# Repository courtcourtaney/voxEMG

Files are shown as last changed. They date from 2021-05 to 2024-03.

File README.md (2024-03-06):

------------

# VoxEMG (v3.1)

## About
<p>This repository contains information and all the editable project files for the VoxEMG project. VoxEMG is a pre-amplificaton circuit developed specifically for surface electromyography (sEMG) of the small extrinsic laryngeal muscles, but can be used on other muscles. <br>
	
The VoxEMG circuit is an extension of the open-source [EMG Circuit v7.1 (Advancer Technologies)](advancertechnologies.com/p/muscle-sensor-emg-circuitkit-bronze.html), from which other EMG platforms such as the Myoware are derived. VoxEMG is specifically aimed to detect activation of the extrinsic laryngeal muscles in both vocalised and subvocalised singing. High-precision and trimmable resistors are used to ensure noise reduction and the circuit is flexible to be used with different types of electrodes for desired implementation. The EMG signals can then be used in a variety of manners, for instance to relay feedback about the singer's movements during practice. <br>

This is an ongoing body of work with origins in my PhD thesis, [Imagining & Sensing: Understanding and Extending the Vocalist-Voice Relationship Through Biosignal Feedback](https://www.courtneynreed.com/assets/pdf/Reed_PhD_ImaginingSensing.pdf), which contains details on how the circuit and sonified EMG biofeedback has been used in vocal practice. I am always adding more information and designs, so please keep an eye out for updates, new implementations and improvements, and feel free to get in contact at any time regarding the project, what you're working on with it, and anything I can help with at: [c.n.reed@lboro.ac.uk](mailto:c.n.reed@lboro.ac.uk) </p>

## Versions

The schematics and PCB designs have been created in and are editable in [KiCad](http://kicad-pcb.org). Please feel free to adapt them to your needs and share your designs with me if you like!

### v3.1 - eTextile Configuration
[Version Subfolder Here](https://github.com/courtcourtaney/voxEMG/tree/master/VoxEMG-v3.1)

The current version's (v3.1) configuration of the circuit is designed for implementations in wearables, featuring mounting loops in the PCB for securing the board to textile structures and castellated inputs (designed by Adan Benito and Becky Stewart for the [Bela E-textile Capelet](https://oshpark.com/shared_projects/y0oSowUt) on Innovate UK), for conductive thread inputs. <br>

<p align="center">
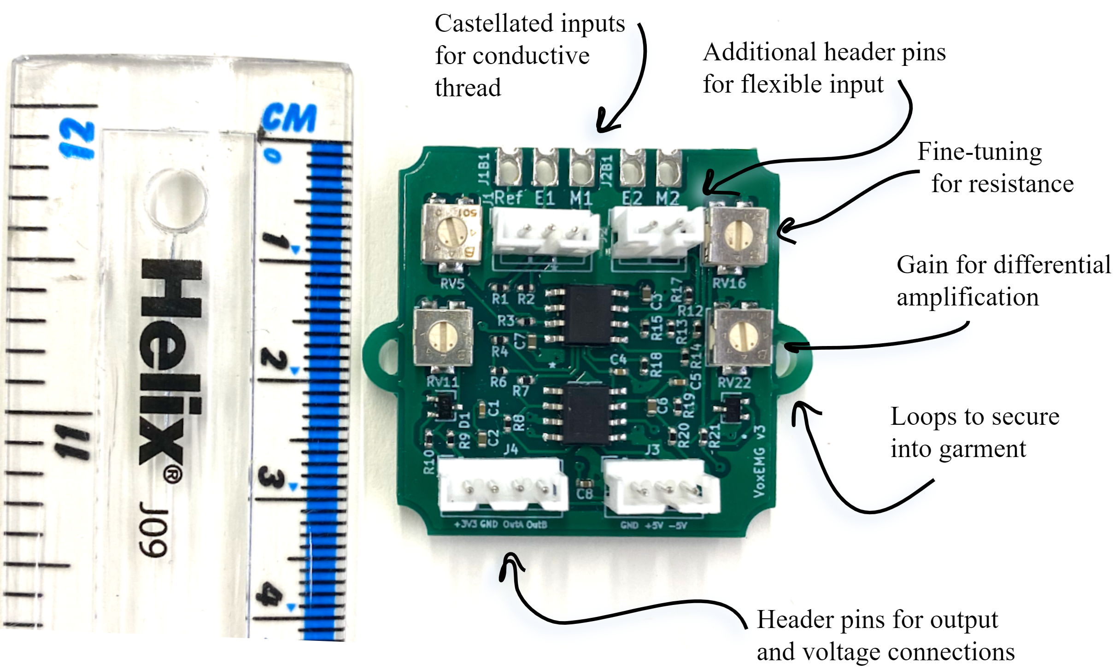
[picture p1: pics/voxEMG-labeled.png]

</p>

### v3.1.2 - Bela Mini Capelet
[Version Subfolder Here](https://github.com/courtcourtaney/voxEMG/tree/master/VoxEMG-v3.1.2)

<p>The latest PCB design (v3.1.2) features the same circuit implemented to be compatible with the Bela Mini embedded audio platforms. This setup is designed to be plug and play, with EMG being received directly on the A0 and A1 analogue inputs of the Bela Mini, and uses similar Molex connectors for electrode inputs. </p>

The design of this v3.1.2 capelet was supported by [Sound & Music UK's New Voices 2022](https://soundandmusic.org/compose/new-voices-2022/) with vocalist Lou Barnell as part of the piece [<em>To Fly Out in the Heat of Day</em>](https://loubarnell.co.uk/TO-FLY-OUT-IN-THE-HEAT-OF-DAY) - thank you!

<p align="center">
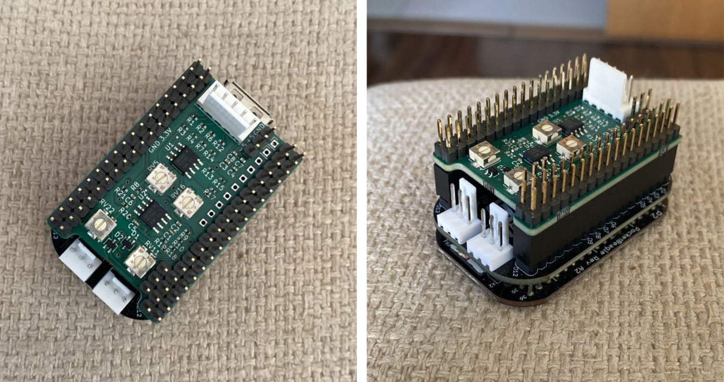
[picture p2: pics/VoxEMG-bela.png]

</p>

## Building the Circuit
If you are interested in getting a VoxEMG board, get in contact - I'm happy to help with any sEMG and vocal projects related projects and I can supply PCBs depending on the project. If you wish to make your own board, it is relatively in-expensive and easy to build the circuit yourself and try it out. A Bill of Materials (BOM) can be found in each version's folder in the file *EMGSensor3.1_bom.xlsx* or listed out below. The setup described here is for single-circuit dual muscle measurement; if you wish to only measure one muscle, you need only use one side of the ICs: <br>

Parts[^1]

* 2x [Texas Instruments OPA1612 op amp](https://www.ti.com/product/OPA1612) <br>
* 5x [Surface cup electrodes](https://www.pulsemedical.co.uk/store/Gold-Reusable-10mm-EEG-Cup-Electrodes-Pack-of-10-Wire-150cm-p79620827)[^2] <br>
* 2x 9V batteries + straps <br>
* Breadboard <br>
* Jumper wires <br>
* Microcontroller of choice or, in our case, a [**Bela**](bela.io)! <br>
* Resistors: <br>
	* 4x 10k Ω 0.1% precison <br>
	* 4x 100k Ω 0.1% precison <br>
	* 2x 100 Ω <br>
	* 2x 1k Ω <br>
	* 6x 10k Ω <br>
	* 2x 100k Ω <br>
	* 2x 150k Ω <br>
* Trimpots/Variable Resistors:<br>
	* 2x 500 Ω <br>
	* 2x 100K Ω <br>
* Capacitors:<br>
	* 1x 0.1 uF ceramic <br>
	* 4x 10 uF ceramic <br>
	* 2x 2.2 nF ceramic <br>
* 2x Schottky 40V 120mA diodes <br><br>

The KiCad project containing the VoxEMG schematics and board layout can be found in the folder for each version *VoxEMG-v3.1,* for the textile-integrated board or *VoxEMG-v3.1.2,* for the Bela Mini capelet, otherwise using the following schematic (v3.1). This schematic depicts use of one side of the ICs - for the second muscle, the connections should be duplicated on the other side. See *VoxEMG-v3.1/EMGSensor3.1.sch* for the full schematic. </p><br>

<p align="center">
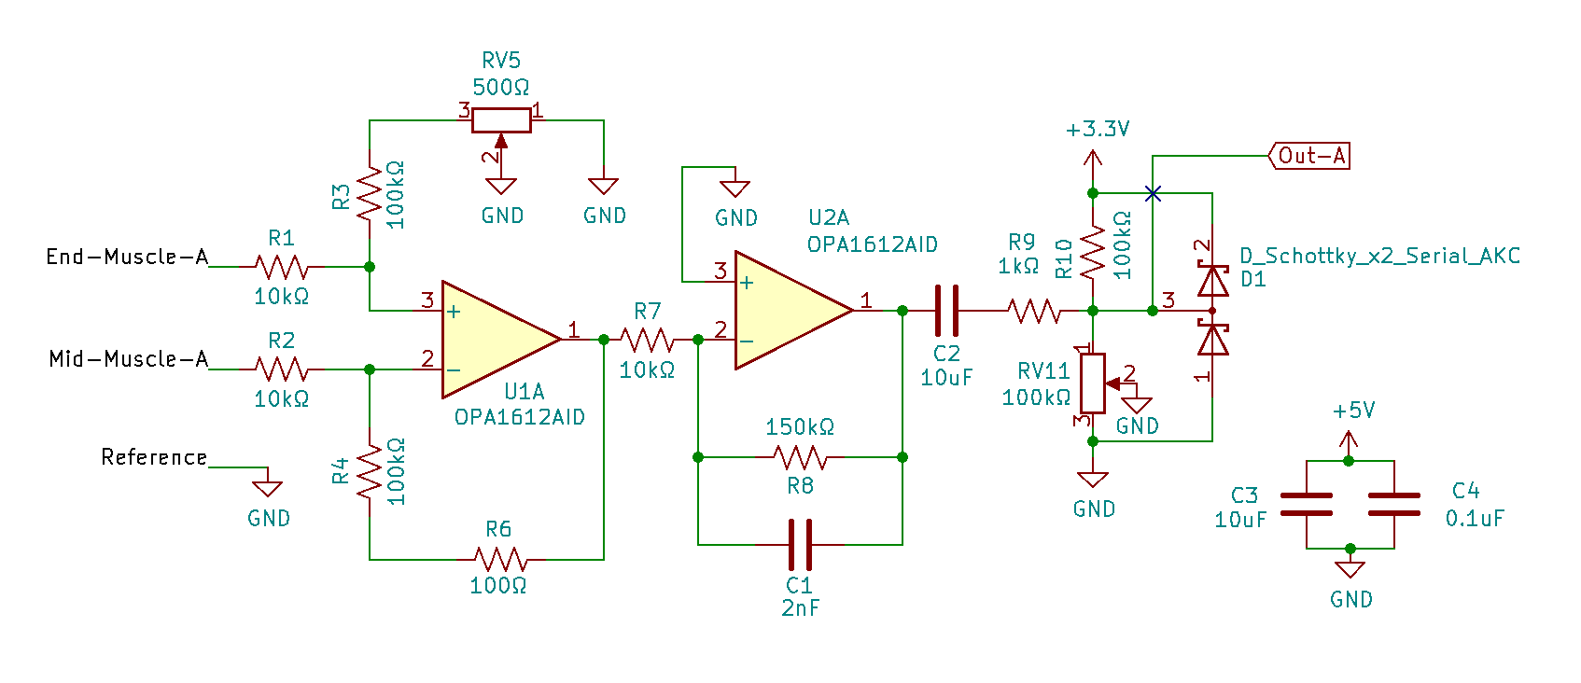
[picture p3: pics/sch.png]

</p>

<!-- *Some notes:* <br> -->
[^1]: Additionally (and especially if you use reusable electrodes), you will need to purchase some adhesive conductive paste (we recommend [Ten20](https://www.pulsemedical.co.uk/store/Ten20-Conductive-Paste-228g-jars-3-pack-10-20-8-p69723951)) and flexible non-woven fabric tape to help secure the electrodes (we use [Hypafix](https://www.bsnmedical.com/products/wound-care-vascular/category-product-search/acute-wound-care/fixation/hypafixr-transparent.html)).

[^2]: These reusable gold-plated silver electrodes use a DIN adaptor intended for use with medical EMG devices; cut these off and you can use either alligator clips to connect these, or solder a male pin to the end of the cable so you can use it in a breadboard or within another cable assembly, such as the Molex connectors implemented in v3.1.2.

<!-- VoxEMG PCB layout          | VoxEMG board
:-------------------------:|:-------------------------:
![](https://github.com/courtcourtaney/voxEMG/blob/master/pics/PCB.png)  |  ![](https://github.com/courtcourtaney/voxEMG/blob/master/pics/3Drender.png) -->

## Example Use
<p>Electrodes will need to be affixed to the muscle site, for instance on the suprahyoid digastric muscle here.</p><br>

<p align="center">

</p>

<p>
We use a Bela for collection of voltages from the EMG, and so the code included here is also for Bela - it is fine to use another microcontroller, so long as you're ok with implementing some simple digital filtering. In this case, we use the analog inputs on Bela.</p><br>

Bela handles some additional filtering of the EMG signal, including:<br>
- DC offset removal (from the DC signal introduced in the voltage divider)<br>
- Notch filtering to remove power line interference (**50Hz** UK - keep in mind if you need to change this wherever you are in the world!)<br>

As well, our setup for studies includes:<br>
- Text file output containing voltages over time<br>
- Setup for a button to be added so the vocalist can press during singing, helping with data/audio synchronisation<br>
You can, of course, comment this out (and it's marked as such in the code).

[Example Code Here](https://github.com/courtcourtaney/voxEMG/tree/master/examples)

## Projects Using the VoxEMG

If you have used the circuit or designs for your project, please let us know so we can add you here!

### Vocal Performances & Collaborations

[<em>To Fly Out in the Heat of Day</em>](https://loubarnell.co.uk/TO-FLY-OUT-IN-THE-HEAT-OF-DAY). Lou Barnell. 2023-2024. Performed in the UK & EU ([Based in Sheffield](https://www.theatredeli.co.uk/Event/enddateto-fly-out-in-the-heat-of-the-day)).

### Research Work & Papers
<span style="font-size:2em;"> 

Courtney N. Reed and Andrew P. McPherson. 2023. <em>The Body as Sound: Unpacking Vocal Embodiment through Auditory Biofeedback.</em> In Proceedings of the Seventeenth International Conference on Tangible, Embedded, and Embodied Interaction (TEI '23). Association for Computing Machinery, New York, NY, USA, Article 7, 1–15. https://doi.org/10.1145/3569009.3572738 [[PDF]](https://www.courtneynreed.com/assets/pdf/Reed_TEI23_BodyAsSound.pdf) <br>

Courtney N. Reed, Sophie Skach, Paul Strohmeier, and Andrew P. McPherson. 2022. <em>Singing Knit: Soft Knit Biosensing for Augmenting Vocal Performances.</em> In Proceedings of the Augmented Humans International Conference 2022 (AHs '22). Association for Computing Machinery, New York, NY, USA, 170–183. https://doi.org/10.1145/3519391.3519412 [[PDF]](https://www.courtneynreed.com/assets/pdf/Reed_AHs22_SingingKnit.pdf) <br>

Courtney N. Reed and Andrew P. McPherson. 2021. <em>Surface Electromyography for Sensing Performance Intention and Musical Imagery in Vocalists.</em> In Proceedings of the Fifteenth International Conference on Tangible, Embedded, and Embodied Interaction (TEI '21). Association for Computing Machinery, New York, NY, USA, Article 22, 1–11. https://doi.org/10.1145/3430524.3440641 [[PDF]](https://www.courtneynreed.com/assets/pdf/Reed_TEI21_sEMGPerformance.pdf) <br>

Courtney N. Reed and Andrew P. McPherson. 2020. <em>Surface Electromyography for Direct Vocal Control.</em> In Proceedings of the International Conference on New Interfaces for Musical Expression (NIME), July 21-25, Birmingham, UK, pp. 458–463. Birmingham Conservatoire, Birmingham, UK. https://doi.org/10.5281/zenodo.4813475 [[PDF]](https://www.courtneynreed.com/assets/pdf/Reed_NIME20_VocalsEMG.pdf) <br>
	
</span>

<br>

## Licensing
<p><br /><span xmlns:dct="http://purl.org/dc/terms/" property="dct:title">VoxEMG</span> by <span xmlns:cc="http://creativecommons.org/ns#" property="cc:attributionName">Courtney N. Reed & Andrew P. McPherson</span> is licensed under a <a rel="license" href="http://creativecommons.org/licenses/by-sa/4.0/">Creative Commons Attribution-ShareAlike 4.0 International License</a>. <br>

In the spirit of open-access research, VoxEMG and the circuit/PBC designs included here are are licensed under a Creative Commons Attribtion Sharealike license, or [CC-BY-SA](https://creativecommons.org/licenses/by-sa/3.0/). The information here is free to use and edit, so long as you provide credit and release your resulting work under the same license. This means you are free to edit and use these designs, as long as you agree to supply credit and release your results under the same license. <br>

If you use these designs or reference them, we ask that you please also cite the following papers in your work: <br>

If you want to create a commercial product using the VoxEMG hardware designs and don't want to release it under the same license, you will need a commercial license. Please email me at [c.n.reed@lboro.ac.uk](mailto:c.n.reed@lboro.ac.uk) to enquire further. </p>

```latex
@inproceedings{Reed_AHs22_SingingKnit,
  title = {{Singing Knit: Soft Knit Biosensing for Augmenting Vocal Performances}},
  author = {Reed, Courtney N. and Skach, Sophie and Strohmeier, Paul and McPherson, Andrew P.},
  year = {2022},
  month = mar,
  booktitle = {{Proceedings of the Augmented Humans International Conference 2022}},
  location = {Kashiwa, Chiba, Japan},
  publisher = {Association for Computing Machinery},
  address = {New York, NY, USA},
  series = {AHs '22},
  pages = {170–183},
  doi = {10.1145/3519391.3519412},
  isbn = {9781450396325},
  url = {https://doi.org/10.1145/3519391.3519412},
  numpages = {14},
  keywords = {wearables, Design, singing, music performance, knit, electromyography, fabric sensors, biosignals},
}
```

```latex
@inproceedings{Reed_NIME20_VocalsEMG,
  title = {{Surface Electromyography for Direct Vocal Control}},
  author = {Reed, Courtney N. and McPherson, Andrew},
  year = {2020},
  month = jul,
  booktitle = {{Proceedings of the International Conference on New Interfaces for Musical Expression}},
  publisher = {Birmingham City University},
  address = {Birmingham, UK},
  pages = {458--463},
  doi = {10.5281/zenodo.4813475},
  issn = {2220-4806},
  url = {https://www.nime.org/proceedings/2020/nime2020_paper88.pdf},
  editor = {Michon, Romain and Schroeder, Franziska},
  presentation-video = {https://youtu.be/1nWLgQGNh0g},
}
```

<!-- 
## To-Do List
There's a lot left to done, but at least for this repository, I'm planning on adding more information, including:<br>
- [x] Include editable schematics and PCB design<br>
- [ ] Step-by-step construction of the circuit<br>
- [ ] Walk-through of identifying laryngeal muscles <br>(feel free to contact me and I will help you via Zoom/Skype if you'd like to learn to do this on yourself!)<br>
- [ ] Add example Supercollider interfacing for sonification of signals/fun<br> -->

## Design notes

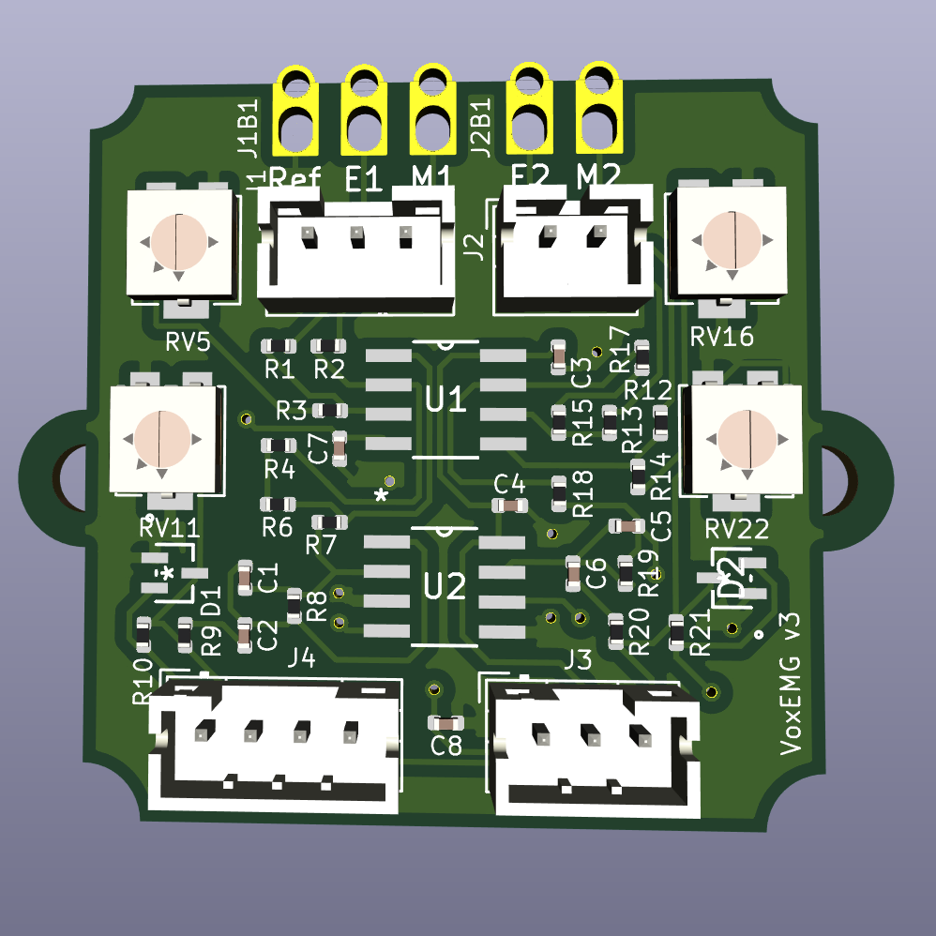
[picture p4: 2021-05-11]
pics/3Drender.png

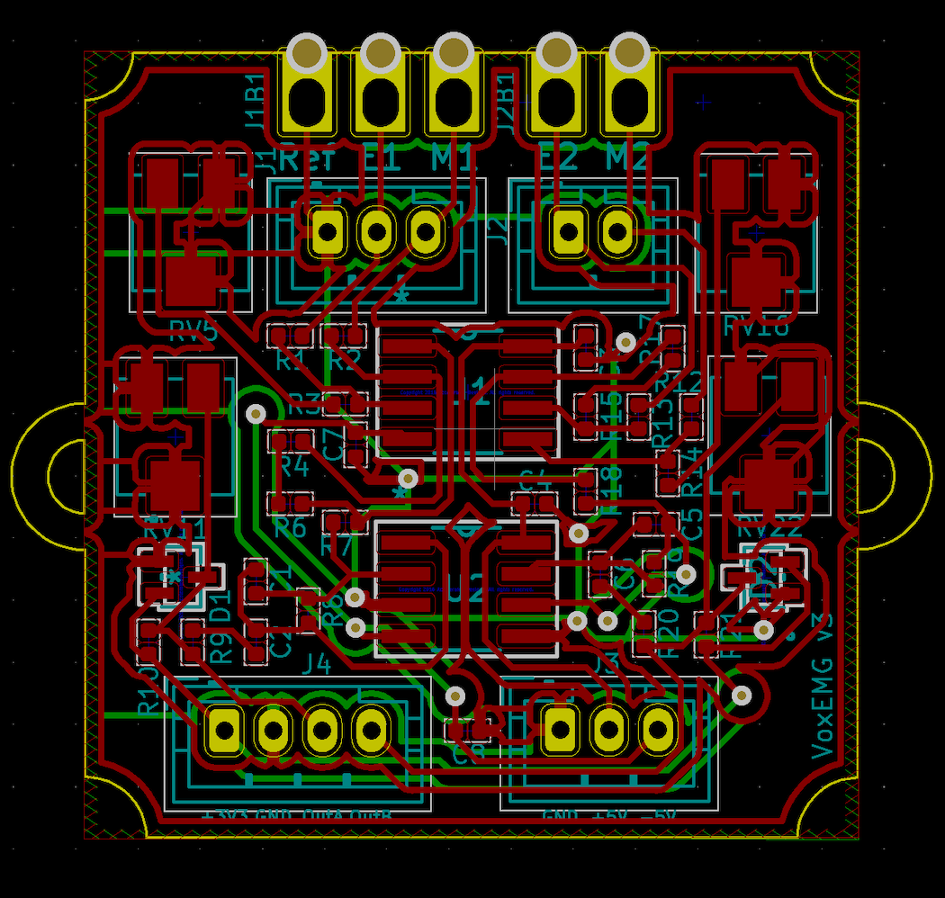
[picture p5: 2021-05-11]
pics/PCB.png

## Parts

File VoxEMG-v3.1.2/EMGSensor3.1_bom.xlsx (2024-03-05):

Name | Quantity | Value | Package | Description | Mouser # | Digi-Key # | Datasheet / Notes
U2, U1 | 2 | OPA1612AID | SOIC-8 | OPA1612AID | 595-OPA1612AID
D1, D2 | 2 | Schottky 40V 120mA | SOT-323-3 | BAS40-04 Schottky diode | 771-BAS40-04W-T/R
C1, C5 | 2 | 2.2nF | "0402" | Capacitor ceramic 0402 | 581-04023C222J4T2A
C8, C4 | 2 | 0.1uF | "0402" | Capacitor ceramic 0402 | 581-04023C104KAT2A62
C2, C3, C6, C7 | 4 | 10uF | "0402" | Capacitor ceramic 0402 | 581-0402ZD106MAT2A
R1, R2, R12, R13 | 4 | 10kOhm | "0402" | Resistor 0402 0.1% | 279-CPF-A-0402B10KE
R3, R4, R14, R15 | 4 | 100kOhm | "0402" | Resistor 0402 0.1% | 279-CPF-A0402B100KE1
R6, R17 | 2 | 100Ohm | "0402" | Resistor 0402 | 603-RP0402BRD07100RL
R7, R18 | 6 | 10kOhm | "0402" | Resistor 0402 | 603-RT0402FRE0710KL
R8, R19 | 2 | 150kOhm | "0402" | Resistor 0402 | RT0402FRE07150KL
R9, R20 | 2 | 1kOhm | "0402" | Resistor 0402 | RT0402FRE071KL
R10, R21 | 2 | 100kOhm | "0402" | Resistor 0402 | 603-RT0402FRE07100KL
RV5, RV16 | 2 | 500Ohm | SMD | Bourns 3314J vertical trim potentiometer | 652-3314J-1-501G
RV22, RV11 | 2 | 100kOhm | SMD | Bourns 3314J vertical trim potentiometer | 652-3314J-1-104E
J1 | 2 | Conn 01x05 | Through-hole | Molex K254 22-27-2051 5-pin male header | 538-22-27-2051
J3, J5, J6, J7, J8, J9, J10 | 7 | Connector_PinHeader | Through-hole | 2mm 01x01 vertical pin header | 910-HDR100IMP40MGVTH

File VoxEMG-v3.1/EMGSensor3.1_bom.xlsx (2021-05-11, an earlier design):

Name | Quantity | Value | Package | Description | Mouser # | Digi-Key # | Datasheet / Notes
U2, U1 | 2 | OPA1612AID | SOIC-8 | OPA1612AID | 595-OPA1612AID
D1, D2 | 2 | Schottky 40V 120mA | SOT-323-3 | BAS40-04 Schottky diode | 771-BAS40-04W-T/R
C1, C5 | 2 | 2.2nF | "0402" | Capacitor ceramic 0402
C8, C4 | 2 | 0.1uF | "0402" | Capacitor ceramic 0402
C2, C3, C6, C7 | 4 | 10uF | "0402" | Capacitor ceramic 0402
R1, R2, R12, R13 | 4 | 10kOhm | "0402" | Resistor 0402 0.1% | 279-CPF-A-0402B10KE
R3, R4, R14, R15 | 4 | 100kOhm | "0402" | Resistor 0402 0.1% | 279-CPF-A0402B100KE1
R6, R17 | 2 | 100Ohm | "0402" | Resistor 0402
R7, R18 | 6 | 10kOhm | "0402" | Resistor 0402
R8, R19 | 2 | 150kOhm | "0402" | Resistor 0402
R9, R20 | 2 | 1kOhm | "0402" | Resistor 0402
R10, R21 | 2 | 100kOhm | "0402" | Resistor 0402
RV5, RV16 | 2 | 500Ohm | SMD | Bourns 3314J vertical trim potentiometer | 652-3314J-1-501G
RV22, RV11 | 2 | 100kOhm | SMD | Bourns 3314J vertical trim potentiometer | 652-3314J-1-104E
J1, J3 | 2 | Conn 01x03 | Through-hole | Connector Header 3 position 2.00mm |  | A98589-ND
J2 | 1 | Conn 01x02 | Through-hole | Connector Header 2 position 2.00mm |  | A98588-ND
J4 | 1 | Conn 01x04 | Through-hole | Connector Header 4 position 2.00mm |  | A98590-ND

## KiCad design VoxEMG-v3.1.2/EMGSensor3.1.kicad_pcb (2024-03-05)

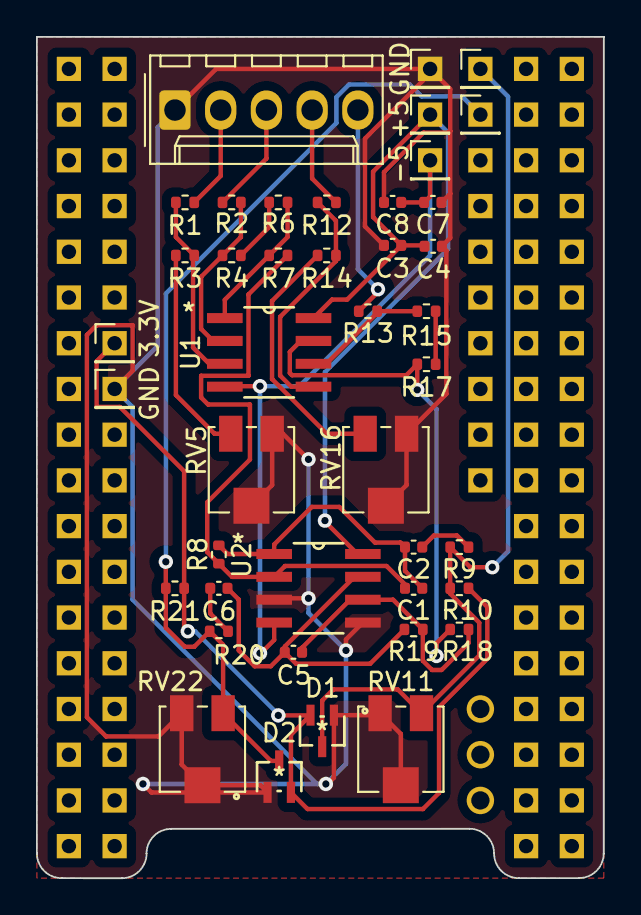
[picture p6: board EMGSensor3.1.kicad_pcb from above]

Board: 2 copper layers, 31.5 x 46.7 mm, 42 parts (0 on the bottom side), 26 nets.

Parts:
3.3V: +3.3V; PinHeader_1x01_P2.00mm_Vertical
+5: +5V; PinHeader_1x01_P2.00mm_Vertical
-5: -5V; PinHeader_1x01_P2.00mm_Vertical
C1: 2nF; C_0402_1005Metric
C2, C3, C6, C7: 10uF; C_0402_1005Metric
C4, C8: 0.1uF; C_0402_1005Metric
C5: 2.2nF; C_0402_1005Metric
D1, D2: D_Schottky_x2_Serial_AKC; BAS40-04W
GND: BelaGND; PinHeader_1x01_P2.00mm_Vertical
GND#2: BatteryGND; PinHeader_1x01_P2.00mm_Vertical
J1: Conn_01x03_Female; Molex_KK-254_AE-6410-05A_1x05_P2.54mm_Vertical
J5: Out-A; PinHeader_1x01_P2.00mm_Vertical
J6: Out-B; PinHeader_1x01_P2.00mm_Vertical
R1, R2, R7, R12, R13, R18: 10kΩ; R_0402_1005Metric
R3, R4, R10, R14, R15, R21: 100kΩ; R_0402_1005Metric
R6, R17: 100Ω; R_0402_1005Metric
R8, R19: 150kΩ; R_0402_1005Metric
R9, R20: 1kΩ; R_0402_1005Metric
RV5, RV16: 500Ω; Potentiometer_Bourns_3314J_Vertical
RV11, RV22: 100kΩ; Potentiometer_Bourns_3314J_Vertical
U1, U2: OPA1612AID

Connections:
+3.3V: 3.3V.1, D1.2 (K), D2.2 (K), R10.1, R21.1
+5V: +5.1, C3.1, C4.2, U1.8 (V+), U2.8 (V+)
-5V: -5.1, C7.2, C8.2, U1.4 (V-), U2.4 (V-)
/End-Muscle-A: J1.2, R1.2
/End-Muscle-B: J1.4, R12.2
/Mid-Muscle-A: J1.3, R2.2
/Mid-Muscle-B: J1.5, R13.2
GND: C3.2, C4.1, C7.1, C8.1, D1.1 (A), D2.1 (A), GND.1, GND#2.1, J1.1, RV5.1, RV5.2, RV11.2, RV11.3, RV16.1, RV16.2, RV22.2, RV22.3, U2.3 (+), U2.5 (+)
unnamed: C1.2, C2.2, R8.2, U2.1
unnamed: C2.1, R9.1
unnamed: C5.2, C6.2, R19.2, U2.7
unnamed: C6.1, R20.1
unnamed: R3.2, RV5.3
unnamed: R4.1, R6.2
unnamed: R6.1, R7.2, U1.1
unnamed: R14.2, RV16.3
unnamed: R15.1, R17.2
unnamed: R17.1, R18.2, U1.7
unnamed: R1.1, R3.1, U1.3 (+)
unnamed: R2.1, R4.2, U1.2 (-)
unnamed: R12.1, R14.1, U1.5 (+)
unnamed: R13.1, R15.2, U1.6 (-)
unnamed: C1.1, R7.1, R8.1, U2.2 (-)
unnamed: C5.1, R18.1, R19.1, U2.6 (-)
Out-A: D1.3 (common), J5.1, R9.2, R10.2, RV11.1
Out-B: D2.3 (common), J6.1, R20.2, R21.2, RV22.1

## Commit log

2020-07-24 Add files via upload
    add circuit schematics
    [EMGSensor2.2.sch]
2020-08-10 Correction to schematic
    R6 should be 100 ohm to ensure the trimming between the two series can be identical, was incorrectly listed at 500 ohm
2020-08-10 fix R6 values in CAD files
    [EMGSensor2.2.sch]
2021-05-11 cleanup, add cad files
    [EMGSensor3.1-B_Cu.gbr, EMGSensor3.1-B_Mask.gbr, EMGSensor3.1-B_Paste.gbr, EMGSensor3.1-B_SilkS.gbr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]
2021-05-11 reorganize project folders
    [EMGSensor2.2.sch]
2024-03-05 add v3.1.2, update README
    [EMGSensor3.1-B_Cu.gbr, EMGSensor3.1-B_Mask.gbr, EMGSensor3.1-B_Paste.gbr, EMGSensor3.1-B_Silkscreen.gbr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]

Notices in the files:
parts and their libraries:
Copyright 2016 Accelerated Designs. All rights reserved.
